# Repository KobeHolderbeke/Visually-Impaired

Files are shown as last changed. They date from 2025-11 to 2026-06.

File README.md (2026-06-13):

# Feel The Score
*Ontwikkelen van een handsfree, toegankelijk systeem dat slechtzienden en blinden helpt muziek intuïtief te leren en te spelen zonder afhankelijk te zijn van traditionele braillepartituren.* 

🛠️ Built by ``Kobe Holderbeke`` & ``Mattea Claeys``   
🔥 Supervised by ``prof. dr. Bas Baccarne``, ``Yannick Christiaens`` & ``Wouter Devriese``    
🌱 Grown at ``Ghent University`` 🏛️ ``Industrial Design Engineering`` ([project overview](https://github.com/basbaccarne/human-centered-design))       

*13/11/2025*   

## Samenvatting
### Probleem 

Slechtziende muzikanten stuiten op grote drempels bij het leren van nieuwe muziek. Braille-bladmuziek is namelijk een complexe, aparte taal die velen niet beheersen. Bovendien moeten muzikanten hun instrument constant loslaten om handmatig door braille-partituren te navigeren, wat de flow onderbreekt en frustratie uitlokt. 

### Onderzoek 

Dit probleem werd vastgesteld via een interview (N = 1). De interviewee stelde: “Ik heb dat (Braille Muziekschrift) wel geleerd, maar ik blijf er zoveel mogelijk van af”. Deze persoon speelt als alternatief de muzikale audiotrack af en leert het doormiddel van perfect pitch*.  

Er blijkt behoefte te zijn aan een efficiënte, handsfree leermethode.

### Oplossing 

Het antwoord op dit probleem is om de muziek in audiovorm, zijnde dat de muziek track of de audio partituur, controleerbaar te maken door de voeten, doormiddel van een slim product. 

### Impact 

Dit neemt zowel de kloof van het leren van een nieuwe taal weg, alsook de frustratie van het loslaten van het instrument, met als hoop het leerproces aangenamer te maken en meer slechtziende mensen aan te zetten om muziek te leren.  

*perfect pitch: Het vermogen om een bepaalde toonhoogte te identificeren of na te bootsen zonder gebruik te maken van een referentietoon.  





---

## Introductie
Dit project ging van start met een algemene challenge: “Spacial Experiences for Visually Impaired Populations”, het ontwikkelen van een slim product dat slechtzienden assisteert in een vorm van ruimtelijke oriëntatie.  

Er wordt gebruikgemaakt van een zekere methode (zie [Methodologie](./docs/methodologie.md)), welke het ontwerpproces opdeelt in vaste fasen.  

Tijdens de eerste fase, [Discovery](./docs/discovery.md), is binnen het ruime probleem (afgeleid uit de challenge), gezocht naar een specifieker deelprobleem: 

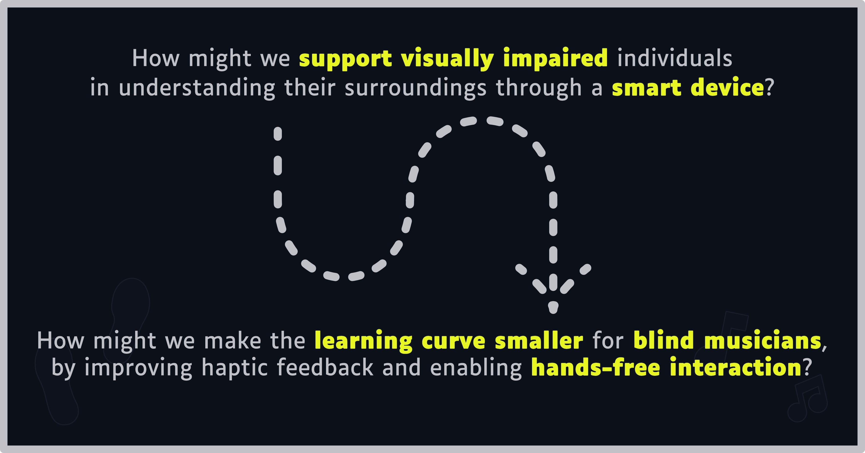
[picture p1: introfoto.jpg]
Introductie


Dit specifieker probleem kadert het project niet rond het vervullen van basisnoden zoals oriëntatie/koken/…, maar wel rond het ondersteunen van ontspanning en zelfexpressie voor slechtziende (aspirant-)muzikanten, door het leerproces van muziek voor hen aangenamer te maken. 
Het brengt volgende hoofddoelen met zich mee:
-	De gebruiker heeft geen kennis van een andere taal nodig, buiten notenleer.
-	De gebruiker moet tijdens het leren het instrument niet loslaten.
-	De gebruiker kan zowel een muziektrack als een audio partituur bedienen.
-	De (eventuele) bijhorende app moet voor slechtzienden toegankelijk zijn.

Ook de boundary conditions:
-	Het product signaleert gebruiksaspecten nooit enkel op visuele wijze.
-	Alle fasen moeten binnen de voorziene deadline (zie [Methodologie](./docs/methodologie.md)) afgewerkt worden.
Aan de hand hiervan wordt in de volgende fase, [Defintion](./docs/definition.md), nagedacht over hoe dit probleem het best kan opgelost worden. Uit inzichten van deze fase alsook uit de volgende fasen, worden zekere eisen geformuleerd waaraan het product moet voldoen (ook in welke mate noodzakelijk), namelijk de [Design Requirements](./docs/design_requirements.md) en ook welke materialen het best gebruikt worden en waar deze aangekocht worden, namelijk de een [Bill of materials](./docs/bom.md).

---

## Inhoudstafel

1. [Methodologie](./docs/methodologie.md)
2. [Discovery](./docs/discovery.md)
3. [Defintion](./docs/definition.md)
4. [Develop phase 1](./docs/Develop_1.md)
5. [Develop phase 2: Antropometrische analyse deel 1](./docs/Develop_phase_2:Antropometrie.md)
6. [Develop phase 2: Antropometrische analyse deel 2](./docs/Antropometrie2.md)
7. [Develop phase 2: Antropometrische analyse deel 3](./docs/Antropo3.md)
8. [Develop phase 2: Prototypes resultaten](./docs/DEV2result.md)
9. [Develop phase 2: Cognitieve analyse](./docs/CognitieveAnalyse.md)
10. [Develop phase 3: CMF Analyse](./docs/CMFanalyse.md)
11. [Develop phase 3: PESTEL Analyse](./docs/PESTELanalyse.md)
12. [Develop phase 3: Resultaten](./docs/DEV3results.md)
13. [Design Requirements](./docs/design_requirements.md)
14. [Bill of materials](./docs/bom.md)

## Conclusie

Het finale concept is een toegankelijke voetcontroller met bijhorende theoretisch uitgewerkte app die blinde en slechtziende muzikanten ondersteunt tijdens het zelfstandig oefenen. De controller maakt het mogelijk om een audio-partituur of muziekfragment te bedienen zonder de handen van het instrument te halen. Functies zoals pauzeren, hervatten, terugspoelen, doorspoelen en herhalen blijven daardoor bereikbaar tijdens het musiceren.

De keuze voor voetbediening sluit goed aan bij de muzikale context. Veel muzikanten zijn al vertrouwd met het gebruik van pedalen, waardoor deze manier van bedienen natuurlijker aanvoelt dan extra knoppen op een scherm of handmatige bediening. Het product vertrekt dus niet vanuit een volledig nieuwe interactie, maar bouwt verder op een handeling die binnen muziek al herkenbaar is.

De fysieke vormgeving is afgestemd op gebruik zonder zicht. Tactiel onderscheidbare knoppen, duidelijke voetpositionering, verstelbare muren, gripvaste materialen en een stabiele bodemplaat zorgen ervoor dat oriëntatie via gevoel mogelijk wordt. Ook de app ondersteunt toegankelijk gebruik door eenvoudige functies, duidelijke structuur en auditieve ondersteuning. Deze keuzes sluiten aan bij de opgestelde [design requirements](docs/design_requirements.md).

Dit concept vormt een sterke oplossing voor het eerder geschetste probleem, omdat het zelfstandigheid, gebruiksgemak en muzikale continuïteit combineert. Tijdens het oefenen ontstaat minder nood aan onderbreking of hulp van buitenaf. Tegelijk blijft het product bewust beperkt tot de belangrijkste functies, waardoor de bediening overzichtelijk blijft en de cognitieve belasting laag blijft.

Naast toegankelijkheid werd ook rekening gehouden met praktische aspecten zoals betaalbaarheid, robuustheid, onderhoud, transport en instelbaarheid voor verschillende lichaamsmaten. Het inklapbare ontwerp en de geïntegreerde handvaten maken het product bruikbaar in een thuis-, school- of oefencontext. Verdere validatie blijft nodig rond langdurig gebruik, materiaalkeuze, knopweerstand en exacte positionering van de bedieningselementen. Toch biedt dit finale concept een geloofwaardige en onderbouwde richting voor een toegankelijk hulpmiddel binnen muziekeducatie.

## Kritische reflectie
De samenwerking binnen de groep verliep vlot en de taken konden goed verdeeld worden. Daardoor konden verschillende onderdelen van het project tegelijk worden uitgewerkt, zoals onderzoek, prototyping, testen en documentatie. Toch had een vroegere planning het proces kunnen versterken, vooral bij het zoeken naar geschikte testpersonen.

Een belangrijke beperking was het beperkte aantal gebruikerstesten. Blinde en slechtziende muzikanten vormen een specifieke doelgroep die moeilijk te bereiken is. De testresultaten leverden daardoor waardevolle inzichten op, maar kunnen niet als volledig representatief gezien worden.

Ook het prototype vraagt nog verdere uitwerking en validatie. Vooral langdurig gebruik, knopweerstand, materiaalkeuze, stabiliteit en app-toegankelijkheid moeten verder getest worden. Daarnaast zijn de app en de render (foto bovenaan de main-page) voorlopig vooral conceptueel uitgewerkt. In een volgende fase kunnen deze onderdelen concreter gebouwd, getest en verfijnd worden. Het concept toont wel aan dat een handsfree voetcontroller een sterke richting kan zijn om zelfstandiger met audio-partituren te oefenen.

## Noot inzake het gebruik van AI
In dit project werd AI gebruikt voor spellings/grammatica controles van teksten en het omzetten van excel tabellen naar github tabellen. In hoofdstukken waarin AI voor andere doeleinden is gebruikt, wordt dit in het hoofdstuk zelf vermeld.

## Bijlagen

Voor een goede view van de bijlagen is openen van word bestanden in de desktop app aangeraden.

### Discovery
* Literatuuronderzoek (N=10)
  * [Protocol](https://ugentbe.sharepoint.com/:w:/t/Group.course1292876/IQB8WhhhP_pdSazPReRh-HxqAclnc3PnnkJyJq7oPYJ3NZ4?e=7g2boN)
  * [Rapport](https://ugentbe.sharepoint.com/:w:/t/Group.course1292876/IQB9HzvLZPKqSpc1Ftse8O0QARGRsxfzFwpFhsLdyy_mlFo?e=11EF0i)
* Interviews (N=3)
  * [Protocol](https://ugentbe.sharepoint.com/:w:/t/Group.course1292876/IQBQU56AthNHTY_BFFeUUjxmASiolwOdjGJiTEfFOpEcLPk?e=OsEMhK)
  * [Rapport](https://ugentbe.sharepoint.com/:w:/t/Group.course1292876/IQBf38VezsivToBSrIhYCN61AUVMqxSsOoYWdKP_1LEdgZQ?e=FsCly7)
    
### Definition
* User testing wave 1 (N=1)
  * [Protocol](https://ugentbe.sharepoint.com/:w:/t/Group.course1292876/IQCpgV68K8tYTbwqrU3BGaQVAbbZWw5pqcu_k0QDw4POE8I?e=BGHP7T)
  * [Rapport](https://ugentbe.sharepoint.com/:w:/t/Group.course1292876/IQAky_YwA6__RZtaeOcWHPhpASCxieU0GRjqjp9feo6laxo?e=5y6nlD)
* User testing wave 2 (N=1)
  * [Protocol](https://ugentbe.sharepoint.com/:w:/t/Group.course1292876/IQBjjLZSffDoT4YwZDXaZOrhAfhvxaoLlUYGOMogOBo6GUY?e=pMHGh2)
  * [Rapport](https://ugentbe.sharepoint.com/:w:/t/Group.course1292876/IQBcQqR74zqURJhRp2q5rA2XAcczsUglUP6ll5FD3lllPYg?e=BxCLvT)

 ### Develop phase 1
* User testing (N=3)
  * [Protocol](https://ugentbe.sharepoint.com/:w:/t/Group.course1292876/IQAjbiEWOX_lQ4XXfaun0UtAAUon7dIECnejuIu1gmOtWKU?e=WpIFe5)
  * [Rapport 1](https://ugentbe.sharepoint.com/:w:/t/Group.course1292876/IQDN2bwuJPMMSLmgR1tbd45yAW7m6enV3AymeFjA8X_QwLY?e=4EHN3X)
  * [Rapport 2](https://ugentbe.sharepoint.com/:w:/t/Group.course1292876/IQC0vbEEvfZeQ49qQybeRaqQAQ82UMk618w59HhCXBCYtpQ?e=vUupAp)

 ### Develop phase 2
* User testing (N=2)
  * [Protocol](https://ugentbe.sharepoint.com/:w:/t/Group.course1292876/IQApzxOackPtQ5DfW1NZEpZ_AazlX7PwUC5u7cyfCQHkbIs?e=VCITgi)
  * [Rapport](https://ugentbe.sharepoint.com/:w:/t/Group.course1292876/IQDsXy24CQZ0SruVJJgNmixlAYmxdDDpnKVGn1WYPvfYCAY?e=BnQCGx)
    
 ### Develop phase 3
* User testing (N=2)
  * [Protocol](https://ugentbe.sharepoint.com/:w:/t/Group.course1292876/IQDxzxEtF3QAR5I6zrbhMU4dAT4qlioyNcmz1yhkrsbSU70?e=lP8Dhw)
  * [Rapport](https://ugentbe.sharepoint.com/:w:/t/Group.course1292876/IQB-Db_cI9J0Srp22GOqeCKyAXsA48JMOGsO7cuSFgdweqc?e=k2Lcjh)

## Licentie

This repository contains both software and design materials created as part of an industrial design energineering project at Ghent University.

- **Software and code:** [MIT License](./LICENSE-MIT)  
- **Design, documentation, CAD, and media:** [CC BY 4.0 License](./LICENSE)
  
You are free to reuse and build upon this work, both commercially and non-commercially, as long as proper attribution is given to the original authors.

## Bronnen
 JohnSmith981. (2025, 7 december). *Absolute pitch*. In Wikipedia. https://en.wikipedia.org/wiki/Absolute_pitch

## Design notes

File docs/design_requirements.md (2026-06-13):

## Overzicht van Design Requirements
|| **Status** || ❌ niet voldaan || ⚠️ gedeeltelijk voldaan || ✅ voldaan ||
## Design Requirements

| **ID** | **Categorie** | **Design R** | **Source** | **Status** |
|---|---|---|---|---|
| AUD-01 | **Auditieve functionaliteit & leerproces** | Het product moet hoofdzakelijk auditieve feedback geven aan de gebruiker. | Interview + Literatuur | ✅ |
| AUD-02 |  | Het product moet ondersteuning bieden voor relatief en absoluut gehoor. | interview + Literatuur | ✅ |
| AUD-03 |  | Het product moet gebruik kunnen maken van talking-scores / audio-partituren. | User-Test 1/2 | ✅ |
| AUD-04 |  | Het product moet audio-partituren handsfree kunnen besturen. | User-Test 1/2 | ✅ |
| AUD-05 |  | Het product moet audio kunnen pauzeren en hervatten. | User-Test 1/2; CognitieveAnalyse.md | ✅ |
| AUD-06 |  | Het product moet audio kunnen door- en terugspoelen en daarbij duidelijke feedback geven. | User-Test 1/2 | ✅ |
| AUD-07 |  | Het product moet een loopfunctie bieden met een duidelijk begin- en eindpunt. | User-Test 1; CognitieveAnalyse.md | ✅ |
| AUD-08 |  | Het product moet onderbrekingen tijdens het oefenen zoveel mogelijk beperken. | Literatuur; discovery.md | ✅ |
| APP-01 | **App & interface** | De app moet intuïtief bedienbaar zijn. | User-Test 1/2 | ✅ |
| APP-02 |  | De belangrijkste app-inputs mogen niet onverwacht van plaats veranderen. | User-Test 2 | ✅ |
| APP-03 |  | De app moet duidelijk maken hoeveel knoppen of inputs per interface beschikbaar zijn. | User-Test 2 | ✅ |
| APP-04 |  | De app moet gelabelde knoppen hebben zodat oriëntatie met VoiceOver mogelijk is. | User-Test 1 | ✅ |
| APP-05 |  | De app moet een intuïtieve en verstaanbare manier bieden om door de muziekcatalogus te navigeren. | User-Test Develop phase 1; Develop_1.md | ✅ |
| APP-06 |  | De app moet een auditieve tutorial of uitleg aanbieden die aan en uit gezet kan worden. | User-Test 1 | ✅ |
| APP-07 |  | De app moet verwarring in lijsten beperken, bijvoorbeeld via duidelijke tabbladen of een vaste navigatiestructuur. | Develop_1.md | ✅ |
| APP-08 |  | Er moet een geschreven of auditief raadpleegbare handleiding beschikbaar zijn met de nodige besturingsinformatie. | Develop_1.md | ✅ |
| UX-01 | **Gebruiksgemak & cognitieve belasting** | Het product moet een lage cognitieve belasting hebben tijdens gebruik. | Literatuur; PESTELanalyse.md | ✅ |
| UX-02 |  | Het product moet intuïtieve inputs bieden voor iedere functie. | User-Test 2; PESTELanalyse.md | ✅ |
| UX-03 |  | Het product moet bruikbaar zijn zonder uitgebreide uitleg of training. | User-Test 1/2 | ✅ |
| UX-04 |  | Het product moet het aantal primaire bedieningsinputs beperken om complexiteit en foutgebruik te verminderen. | User-Test 2; PESTELanalyse.md | ✅ |
| UX-05 |  | De gebruiker moet functies kunnen aan- of uitzetten zodat een basis- en gevorderde gebruikservaring mogelijk is. | PESTELanalyse.md | ⚠️ |
| UX-06 |  | Het ontwerp moet inspelen op gewoontes van de gebruiker en onnodige functies vermijden. | User-Test 2 | ✅ |
| ACC-01 | **Toegankelijkheid & inclusie** | Het product moet bestuurbaar zijn met minimale tactiele leesvaardigheid. | Interview | ✅ |
| ACC-02 |  | Het product moet zonder handen bediend kunnen worden. | User-Test 1 | ✅ |
| ACC-03 |  | Het product moet zelfstandig bruikbaar zijn voor blinde en slechtziende gebruikers zonder visuele ondersteuning. | CMFanalyse.md; README.md | ✅ |
| ACC-04 |  | Het product mag nooit uitsluitend visueel communiceren; belangrijke informatie moet ook tactiel, auditief of haptisch waarneembaar zijn. | README.md; CMFanalyse.md | ✅ |
| ACC-05 |  | De kleuren moeten voldoende contrast bieden tussen basis, knoppen en markeringen voor slechtziende gebruikers. | CMFanalyse.md | ✅ |
| ANT-01 | **Antropometrische maatvoering** | Het ontwerp moet voetmaten van de volledige doelgroep ondersteunen: grootste voet mannen 18–65 P99 = 289 mm voetlengte en 114 mm voetbreedte; kleinste voet meisjes 6 P1 = 157 mm voetlengte en 60 mm voetbreedte. | Develop_phase_2:Antropometrie.md | ✅ |
| ANT-02 |  | Voor de bepaling van knop-/contactposities moeten de Belgische schattingen gebruikt worden: mannen 18–65 P99 = 216,5 mm ballengte en 25,8 mm verticale afstand tussen maximale breedtepunten; meisjes 6 P1 = 109,4 mm ballengte en 15,2 mm verticale afstand. | Develop_phase_2:Antropometrie.md | ✅ |
| ANT-03 |  | De contact-/inputranges moeten met veiligheidsmarge afgerond worden naar 30 mm en 40 mm; dit komt uit 24,9 mm → 30 mm en 35,5 mm → 40 mm. | Develop_phase_2:Antropometrie.md | ✅ |
| ANT-04 |  | De voet-tot-voetafstand moet de geschatte extremen van de doelgroep ondersteunen: 105 mm tot 340 mm, afgerond naar een instelbereik van 100 mm tot 350 mm. | Antropometrie2.md | ✅ |
| ANT-05 |  | De dimensionering van de voetplaatsing moet rekening houden met heupbreedtes: mannen 18–65 P99 = 430 mm, vrouwen 18–65 P99 = 483 mm, jongens 6 P1 = 175 mm en meisjes 6 P1 = 180 mm. | Antropometrie2.md | ✅ |
| ANT-06 |  | De hoogte van de muren moet onderbouwd worden met de geschatte maximale voethoogte: P99 instaphoogte = 70,4 mm en Belgische schatting = 76,68 mm; de gekozen muurhoogte blijft 30 mm. | Antropometrie2.md | ✅ |
| ANT-07 |  | De handvatdimensionering moet rekening houden met handmaten van de doelgroep: handlengte 109–218 mm, handbreedte 51–98 mm, maximale handdikte 36 mm en maximale vingerdikte 17,8 mm. | Antropo3.md | ✅ |
| PHY-01 | **Fysiek ontwerp & ergonomie** | Het product moet een stabiele ergonomische rustpositie bieden. | User-Test 1 | ✅ |
| PHY-02 |  | Het product moet signifiers bieden om plaatsing, oriëntatie en gebruik duidelijk te maken. | User-Test 2; definition.md | ⚠️ |
| PHY-03 |  | Er moet een duidelijk tactiel verschil zijn tussen voetzones en knop-/behuizingszones. | DEV2result.md | ⚠️ |
| PHY-04 |  | Het product moet zo compact mogelijk zijn, met voorkeur voor verticale compactheid boven horizontale compactheid. | User-Test Develop phase 1; Develop_1.md | ✅ |
| PHY-05 |  | De bediening moet zo weinig mogelijk voetverplaatsing vereisen. | User-Test Develop phase 1; Develop_1.md | ✅ |
| PHY-06 |  | Het product mag bij langdurig gebruik geen negatieve lichamelijke gevolgen veroorzaken, zoals krampen of pijn. | Develop_1.md | ✅ |
| PHY-07 |  | De knopposities moeten bruikbaar zijn voor een brede range aan voetgroottes. | Develop_phase_2:Antropometrie.md | ✅ |
| PHY-08 |  | De knoppen moeten bereikbaar zijn zonder oncomfortabele voetrotatie of overdreven voetverplaatsing. | Develop_phase_2:Antropometrie.md | ✅ |
| PHY-09 |  | De bodemplaat moet finaal 485 mm lang en 320 mm breed zijn. | Antropometrie2.md | ✅ |
| PHY-10 |  | De zijwaartse muren moeten de voeten begrenzen met een muurgedeelte van 160 mm lang en een klemstuk van 31 mm lang. | Antropometrie2.md | ✅ |
| PHY-11 |  | De muren moeten een breedte van 10 mm hebben; de klemstukjes moeten 4,6 mm breed/hoog zijn zodat ze met tolerantie in de roosters schuiven. | Antropometrie2.md | ✅ |
| BTN-01 | **Knoppen & inputgedrag** | Per voet moeten twee knopcontactzones voorzien worden: een kleine knop/contactrange van 30 mm en een grote knop/contactrange van 40 mm. | Develop_phase_2:Antropometrie.md; Antropometrie2.md | ✅ |
| BTN-02 |  | De knoppen moeten 20 mm hoog zijn, 10 mm dik zijn en in niet-ingedrukte stand ongeveer 7,7 mm uit de muur steken. | Antropometrie2.md | ✅ |
| BTN-03 |  | Het indrukinterval van de knop moet ongeveer 5 mm bedragen als balans tussen misinputpreventie, compactheid, stevigheid en snelheid. | Antropometrie2.md | ✅ |
| BTN-04 |  | De schuif-/behuizingslepjes van de knoppen moeten ongeveer 9,8–10 mm hoog zijn, aan beide zijden 15 mm lang zijn en een schuifstukdikte van 1,8 mm hebben. | Antropometrie2.md | ✅ |
| BTN-05 |  | Het product moet ongewenste interpretatie van gebruik zoveel mogelijk vermijden. | User-Test Develop phase 1; Develop_1.md | ✅ |
| BTN-06 |  | De bediening moet zo snel mogelijk reageren binnen de context van muziek oefenen. | User-Test Develop phase 1; Develop_1.md | ✅ |
| BTN-07 |  | Het product moet het risico op verkeerde inputs minimaliseren. | User-Test Develop phase 1; Develop_1.md | ✅ |
| BTN-08 |  | Het product moet een nauwkeurige response geven op inputs. | Develop_1.md | ✅ |
| BTN-09 |  | Het product moet een merkbare vorm van haptische of trilfeedback bieden op inputs. | User-Test Develop phase 1; Develop_1.md | ⚠️ |
| BTN-10 |  | De knoppen moeten tactiel duidelijk onderscheidbaar zijn door verschil in textuur, vorm, grootte of afwerking. | CMFanalyse.md | ⚠️ |
| BTN-11 |  | De knoppen moeten voldoende grip bieden zodat de voet niet wegglijdt tijdens het bedienen. | CMFanalyse.md | ✅ |
| BTN-12 |  | Pauzeren moet op de meest toegankelijke input geplaatst worden. | CognitieveAnalyse.md | ✅ |
| BTN-13 |  | Terugspoelen moet bij voorkeur links geplaatst worden, omdat gebruikers links spontaan met teruggaan associëren. | CognitieveAnalyse.md | ✅ |
| SAFE-01 | **Foutpreventie & veiligheid** | Het systeem moet misinputs opvangen zonder de flow van de gebruiker te onderbreken. | PESTELanalyse.md | ✅ |
| SAFE-02 |  | Bij gelijktijdig of foutief indrukken van knoppen mag geen ongewenste actie uitgevoerd worden. | PESTELanalyse.md | ✅ |
| SAFE-03 |  | Het ontwerp moet misinputs bij grotere voeten voorkomen door voldoende ruimte, geschikte knopweerstand of een aangepaste inputvorm. | Develop_phase_2:Antropometrie.md | ✅ |
| SAFE-04 |  | Het product moet een antisliponderzijde hebben, bijvoorbeeld rubberen voetjes of een rubberen laag. | CMFanalyse.md | ✅ |
| SAFE-05 |  | De randen en overgangen van de behuizing moeten veilig en afgerond afgewerkt zijn. | CMFanalyse.md | ✅ |
| ADJ-01 | **Instelbaarheid & modulariteit** | De voetplaatsing moet instelbaar zijn zodat verschillende voetbreedtes en voetafstanden comfortabel ondersteund worden. | Antropometrie2.md | ✅ |
| ADJ-02 |  | De verstelbaarheid van het product moet voelbaar en vanzelfsprekend zijn. | DEV2result.md | ✅ |
| ADJ-03 |  | De gebruiker moet tactiel kunnen voelen wanneer een onderdeel vast of los staat. | DEV2result.md | ✅ |
| ADJ-04 |  | Het verstellen van de muurtjes moet zonder losse onderdelen kunnen gebeuren. | DEV2result.md | ⚠️ |
| ADJ-05 |  | De knoppen en/of begrenzende muren moeten mee kunnen bewegen met de ingestelde voetpositie. | Antropometrie2.md | ✅ |
| ADJ-06 |  | De begrenzende muren moeten in elke instelling voldoende vast staan om de voet te geleiden en bedieningskrachten op te vangen. | Antropometrie2.md | ✅ |
| ADJ-07 |  | Onderdelen en elektronica moeten afzonderlijk vervangbaar zijn zodat niet het volledige product vervangen moet worden. | PESTELanalyse.md; CMFanalyse.md | ✅ |
| ADJ-08 |  | De verschuifbare muren moeten vastgezet worden in een dubbel roostersysteem met zowel een borgingsafstand als tussenborgingsafstand van 5 mm. | Antropometrie2.md | ✅ |
| ADJ-09 |  | De rail van het dubbele roostersysteem moet 42 mm hoog zijn. | Antropometrie2.md | ✅ |
| ADJ-10 |  | Het eerste rooster moet van 12 mm tot 22 mm boven de bodemplaat lopen, met 12–17 mm voor borging en 17–22 mm voor het schuifstuk. | Antropometrie2.md | ✅ |
| ADJ-11 |  | Het tweede rooster moet van 27 mm tot 37 mm boven de bodemplaat lopen, met 27–32 mm voor borging en 32–37 mm voor het schuifstuk. | Antropometrie2.md | ✅ |
| ADJ-12 |  | De kant van de rail bij de referentiemuur moet over de eerste 55 mm geen dubbel rooster bevatten, zodat de werking intuïtiever wordt en onnodige uitsluiting beperkt blijft. | Antropometrie2.md | ✅ |
| ADJ-13 |  | Eén van de vier muren moet volledig links, vanuit gebruikersperspectief, vast aan de rail staan als referentiemuur/nulpunt; de andere drie muren moeten verschuifbaar zijn. | Antropometrie2.md | ✅ |
| ADJ-14 |  | De rail moet een algehele dikte van 15 mm hebben, waarvan 10 mm massief is en 5 mm uit uitsnijdingen/groeven voor de roosters bestaat. | Antropometrie2.md | ✅ |
| ADJ-15 |  | De muren moeten stevig borgen met staven: 3 mm diameter voor verticale blokkering door het bovenste rooster en 5 mm diameter voor horizontale blokkering door de bodemplaat. | Antropometrie2.md | ✅ |
| ADJ-16 |  | De borgingsbouten en gaten moeten op tolerantie gedimensioneerd worden: verticale bout 5 mm met gat 5,1 mm; horizontale bout 2,8 mm met gat 3 mm. | Antropometrie2.md | ✅ |
| CMF-01 | **Materiaal, CMF & afwerking** | De knoppen moeten bij voorkeur gemaakt worden uit TPU of een gelijkaardig gripvast en slijtvast materiaal. | CMFanalyse.md | ⚠️ |
| CMF-02 |  | De behuizing moet stevig, vormvast en bestand zijn tegen gebruik op de grond. | CMFanalyse.md | ✅ |
| CMF-03 |  | De behuizing moet bij voorkeur gemaakt worden uit ABS-kunststof wegens de balans tussen kostprijs, sterkte, gewicht en produceerbaarheid. | CMFanalyse.md | ⚠️ |
| CMF-04 |  | De behuizing moet een matte afwerking hebben om reflecties voor slechtziende gebruikers te beperken. | CMFanalyse.md | ✅ |
| CMF-05 |  | De behuizing moet plaatselijk licht getextureerd zijn om tactiele herkenbaarheid te ondersteunen. | CMFanalyse.md | ⚠️ |
| CMF-06 |  | Het kleurgebruik moet beperkt en functioneel blijven zodat het product duidelijk en niet verwarrend oogt. | CMFanalyse.md | ✅ |
| DUR-01 | **Duurzaamheid & onderhoud** | Het product moet stevig en robuust genoeg zijn voor herhaald fysiek gebruik met de voeten. | PESTELanalyse.md; CMFanalyse.md | ✅ |
| DUR-02 |  | De zijkanten van de knoppen moeten bestand zijn tegen herhaald aantikken met de voet. | CMFanalyse.md | ✅ |
| DUR-03 |  | De gekozen materialen moeten slijtvast zijn en bestand tegen wrijving, druk, stof en vuil. | CMFanalyse.md | ✅ |
| DUR-04 |  | Het product moet eenvoudig schoon te maken zijn met een vochtige doek. | CMFanalyse.md | ⚠️ |
| DUR-05 |  | De texturen mogen niet te diep zijn, zodat stof en vuil zich niet gemakkelijk ophopen. | CMFanalyse.md | ✅ |
| DUR-06 |  | Het product moet zo weinig mogelijk naden, spleten en openingen bevatten. | CMFanalyse.md | ✅ |
| DUR-07 |  | Onderdelen die veel slijtage krijgen, zoals de knoppen, moeten indien mogelijk vervangbaar zijn. | CMFanalyse.md | ✅ |
| TRN-01 | **Transport & opbergen** | De bodemplaat moet inklapbaar of compact opbergbaar zijn zonder de bruikbaarheid tijdens het spelen te verminderen. | Antropometrie2.md | ✅ |
| TRN-02 |  | Het product moet automatisch of semiautomatisch beginnen dichtklappen wanneer het wordt opgetild. | DEV2result.md | ✅ |
| TRN-03 |  | Het handvat moet geïntegreerd blijven in de vorm van het product. | DEV2result.md | ✅ |
| TRN-04 |  | Het product moet stabiel blijven tijdens het ronddragen. | DEV2result.md | ✅ |
| TRN-05 |  | De bodemplaat moet in twee gelijke delen worden verdeeld met een horizontale snijlijn haaks op de voetlengterichting, zodat het prototype kan inklappen. | Antropometrie2.md | ✅ |
| TRN-06 |  | Aan weerszijden moeten handvatgaten voorzien worden die bij inklapping aligneren, zodat ze samen als één handvat gebruikt kunnen worden. | Antropometrie2.md | ✅ |
| TRN-07 |  | Het handvat moet een lengte van 100 mm krijgen zodat handen binnen de doelgroep in het handvat passen. | Antropo3.md | ✅ |
| TRN-08 |  | Het handvat moet een breedte/dikte van 35 mm over de kritische lengte krijgen zodat handen binnen de doelgroep comfortabel passen. | Antropo3.md | ✅ |
| TRN-09 |  | De handvat-tot-randafstand moet 22 mm bedragen zodat gebruikers binnen de doelgroep het product goed kunnen vastklemmen tijdens het dragen. | Antropo3.md | ✅ |
| BUS-01 | **Kostprijs & haalbaarheid** | De kostprijs moet laag genoeg blijven om het product toegankelijk te houden voor de doelgroep. | CMFanalyse.md; PESTELanalyse.md | ✅ |
| BUS-02 |  | De gewenste functionaliteit, robuustheid, contrast en textuur moeten tegen een zo laag mogelijke kostprijs bereikt worden. | PESTELanalyse.md | ✅ |
| DAT-01 | **Privacy & data** | De app moet zo weinig mogelijk persoonlijke gegevens opslaan en duidelijk communiceren welke data gebruikt wordt. | PESTELanalyse.md | ⚠️ |
| DAT-02 |  | Het ontwerp moet vermijden dat gebruikers een extra account moeten aanmaken, tenzij dit noodzakelijk blijkt uit gebruikerstests. | PESTELanalyse.md | ⚠️ |

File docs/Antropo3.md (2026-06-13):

# Develop 2 – Antropometrische Studie
## Deel III: Analyse van Handafmetingen – Dimensionering van handvat
### 1 Onderzoeksdoel

Het doel van dit onderzoek is om de plaatsing en afmetingen voor het handvat (Figuur 2) van een nieuwe prototype iteratie (Figuur 1) te definiëren. Zie Deel I: Analyse van Voetafmetingen – Dimensionering van Bakje en Deel II: Analyse van Heup- en Beenafmetingen – Plaatsing van Bakjes voor een beschrijving en conceptuele weergave van de verwachte functionaliteiten van dit prototype. Deze onbekenden worden bepaald doormiddel van een antropometrische analyse, gebruikmakend van bestaande betrouwbare antropometrische gegevens van de hand.

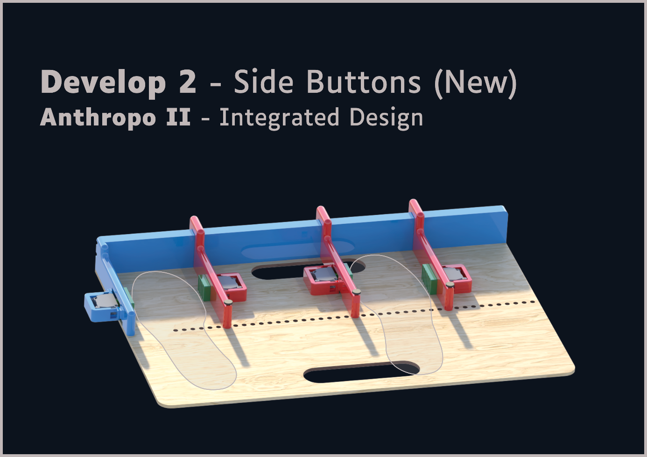
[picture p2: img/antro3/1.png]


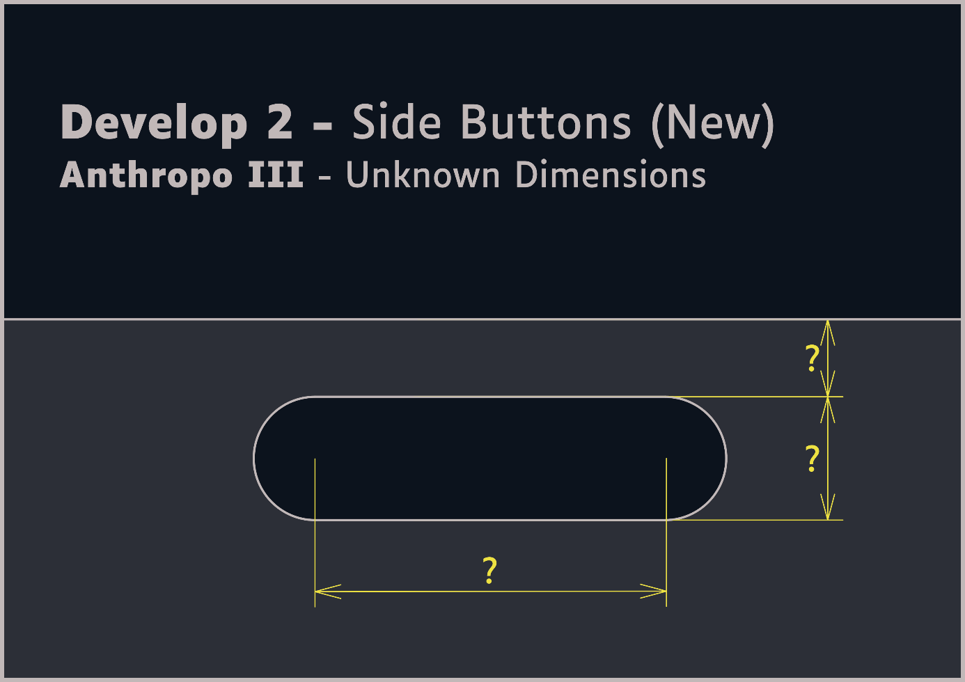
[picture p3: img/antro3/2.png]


### 2 Motivatie

Gezien de mogelijke toepassing dat dit product door muziekstudenten gebruikt zou worden en in naam van het algemene streefdoel om transportatie toegankelijk te maken, wordt gekozen om handvaten toe te voegen om hierbij te helpen. Het idee is niet om het horizontaal als een dienblad vast te houden, maar om de bodemplaat inklapbaar te maken, waardoor de handvaten langs weerskanten aligneren en het kan gedragen worden als soort handkoffer. Dit principe wordt in Figuur 3 afgebeeld.

Het is dan gewenst dat deze handvaten voor de gehele doelgroep voor ogen (“kleinste” jongens/meisjes van 6 jaar (P1) tot “grootste” mannen/vrouwen tussen de 18 en 65 jaar (P99)) bereikbaar en bruikbaar zijn, vandaar dit onderzoek.

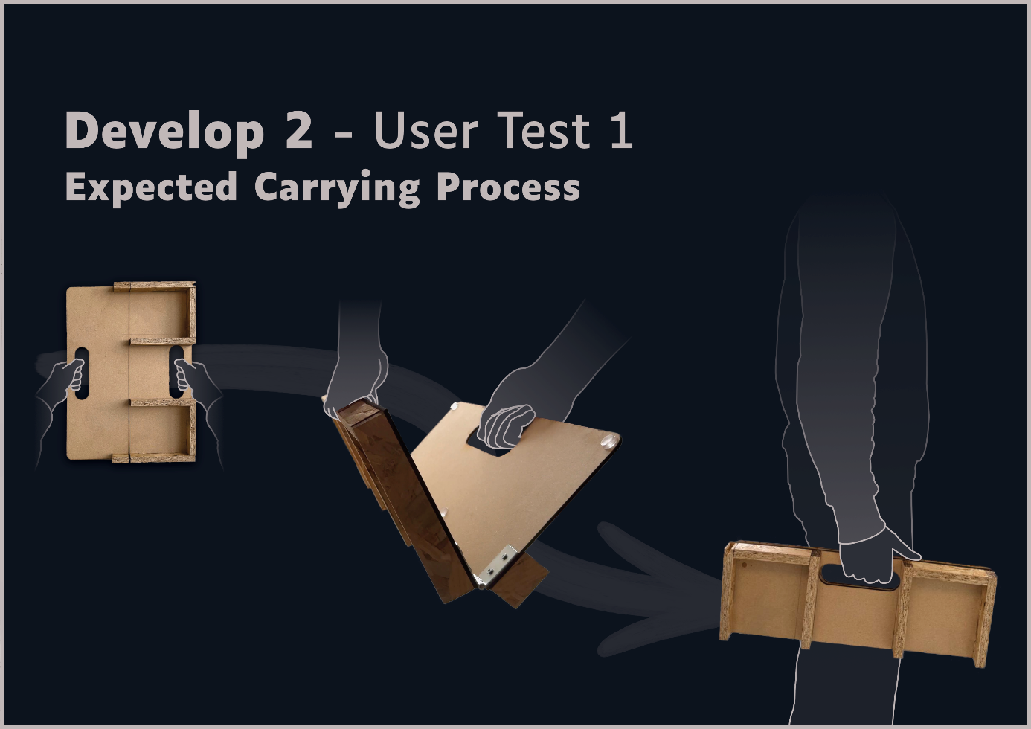
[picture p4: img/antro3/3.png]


### 3 Data

Als bron aan antropometrische gegevens wordt DINBelg gebruikt. 

De interessante gegevens zijn:
-	Handlengte
-	Handbreedte
-	Handdikte

Deze gegevens zijn verzameld in Tabel 1:

| Populatiebeschrijving | Handlengte (mm) | Handbreedte (mm) | Handdikte (mm) |
|---|---:|---:|---:|
| Mannen, 18-65, P99 | 218 | 98 | 36 |
| Vrouwen, 18-65, P99 | 202 | 85 | 33 |
| Jongens, 6, P1 | 111 | 51 | / |
| Meisjes, 6, P1 | 109 | 52 | / |

### 4 Data analyse

De handlengte varieert tussen 109mm en 218mm.

De handbreedte varieert tussen 51mm en 98mm.

De maximale handdikte is 36mm.

#### 4.1 Dimensionering van concept

Voor de lengte van het handvat wordt 100mm genomen, om de gehele range [51, 98] te accommoderen.

De breedte van het handvat wordt op 35mm genomen. Op het eerste zicht lijkt dit te klein aangezien de maximale handdikte 36mm is, maar in de holte van het handvat komen enkel de vingers terecht, niet het volledige hand.

De dikte van de hand aan de vingers wordt benaderd doormiddel van een antropometrische studie van Rogers et al. (2008). Hierin wordt de vingerdikte gemeten als de afstand tussen de palm en de rug van de vinger, aan de verschillende gewrichten. De maximale dikte hierbij bedraagt 17,8mm zelfs met een grote factor erbij gerekend in naam van onzekerheid van schatting, zal 35mm nog steeds ruim voldoende zijn.

Wat de implicaties van de handlengtes zijn, ligt ook iets complexer. Het prototype kan immers op verschillende manieren vastgehouden worden tijdens het ronddragen, zoals afgebeeld in Figuur 4:

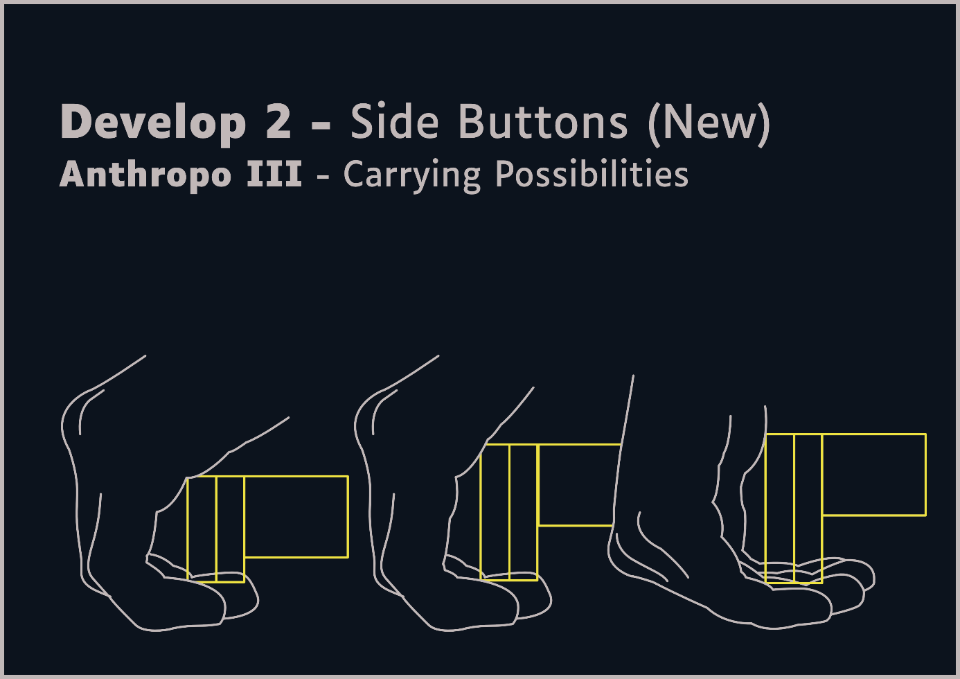
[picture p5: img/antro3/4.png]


Hoewel je in principe het prototype in de hand zou kunnen laten vallen, zonder deze bovenaan vast te klemmen, zoals te zien in de derde situatie van Figuur 4, kan dit voor discomfort zorgen, aangezien het gehele gewicht geconcentreerd is op hetzelfde punt, vergelijkbaar met het ronddragen van een plastic zak.

De grootste inklemming en bijgevolg gewichtsverdeling, zo ook comfort, is bij het vasthouden zoals in de eerste situatie van Figuur 4.

De inschatting wordt gemaakt dat zo’n inklemming haalbaar is als de te “overbruggen” afstand, dus de afstand tussen het handvat en de rand, ongeveer een vierde van de handlengte bedraagt.

Dit zou betekenen:

109mm * 1/4 =27,25mm

Rekening houdend met het feit dat deze schatting zuiver gebaseerd is op intuïtie, wordt gekozen voor een afstand van 22mm. Dit zou het product comfortabel vast neembaar moeten maken (testen ter validatie), zonder de structurele integriteit in gevaar te brengen. 

---

#### 4.2 Analyse van dimensionering

Hieruit volgen als samenvatting volgende dimensies:

  -	Handvatbreedte (minus afronding, dus enkel voor het stuk met eenzelfde breedte): 100mm

  -	Handvatdikte: 35mm

  -	Handvat-tot-rand afstand: 22mm
  
Deze dimensies worden ook verzameld en geïllustreerd in Figuur 5:

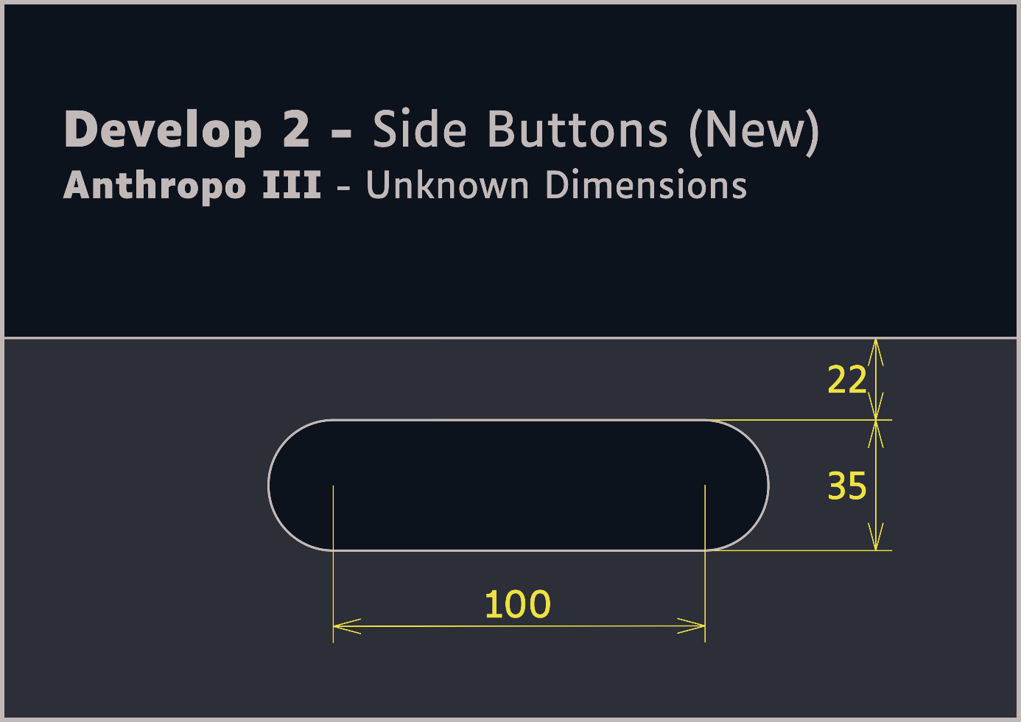
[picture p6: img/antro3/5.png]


---

### 5 Conclusie

Uit het onderzoek komen volgende nieuwe design requirements voort:

-	Om de handen van iedereen binnen de doelgroep in het handvat te laten passen, krijgt deze een lengte van 100mm.

-	Om de handen van iedereen binnen de doelgroep in het handvat te laten passen en comfortabel te laten zitten, krijgt deze een breedte van 35mm over de gehele kritische lengte.

-	Om iedereen binnen de doelgroep het product goed te laten vastklemmen bij het dragen, wordt de handvat-tot-rand lengte 22mm.

### 6 Literatuurlijst
#### 6.1 Internetpagina's

DINBelg. (2005). DINBelg. https://www.dinbelg.be
Rogers, M. S., Barr, A. B., Kasemsontitum, B., & Rempel, D. M. (2008). A three-dimensional anthropometric solid model of the hand based on landmark measurements. Ergonomics, 51(4), 511–526. https://doi.org/10.1080/00140130701710994 

#### 6.2 Generatieve AI

Generatieve AI (ChatGPT, OpenAI) is gebruikt ter ondersteuning bij het toepassen van APA-richtlijnen, waaronder het correct formatteren van bronvermeldingen en het verwijzen naar figuren en citaten. De output is gecontroleerd en waar nodig aangepast door de auteur.

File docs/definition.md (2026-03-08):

## Definition
Het doel van de Definition fase is om een antwoord te vinden op de vraag:  

_“Hoe kunnen we de leercurve voor slechtziende muzikanten verkleinen door de haptische feedback te verbeteren en interactie zonder handen mogelijk te maken?” [Introductie](/README.md)_ 

Dit vindt plaats onder de vorm van twee waves, door het volgen van een vast proces [Methodologie](/docs/methodologie.md): 
- Brainstormen _(Functies, vormgeving)_
- Schetsen _(Conceptuele uitwerking)_
- Prototypen _(Materialisatie)_
- Testen _(Validatie/verbetering/eliminatie, inzichten, N = 2)_

---
### Wave 1 

**Brainstorm** 

Er kon gewerkt worden met intuïtie, Discovery interviews en benchmarking om te veronderstellen wat het product zou moeten doen en hoe het er zoal zou kunnen uitzien. 

Eerst werden de functies bepaald: 

Het product moet de gebruiker in staat stellen de muziektrack, audiopartituur te kunnen: 
- Pauzeren
- Hervatten
- Doorspoelen
- Terugspoelen 

Voor de vormgeving waren relevante inzichten uit benchmarking dat compactheid een grote rol speelt en dat vaak gebruikgemaakt wordt van metaforen. _(vormen/functies van alledaagse producten die al bij mensen bekend zijn)._ 

Hierdoor kwam het idee van twee pedalen _(1 per voet)_, vergelijkbaar met gitaarpedalen: 

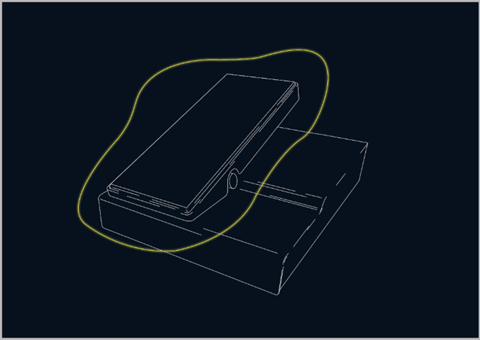
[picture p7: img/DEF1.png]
PEDAAL


**Schetsen** 

Rekening houdend met de vooropgestelde eigenschappen komt het schetsproces uit op 2 compacte indrukbare “blokjes”, geïnspireerd door gitaarpedalen. 

Zoals weergegeven bieden deze 2 pedalen genoeg inputmogelijkheden om de vooropgestelde functies te kunnen uitvoeren.

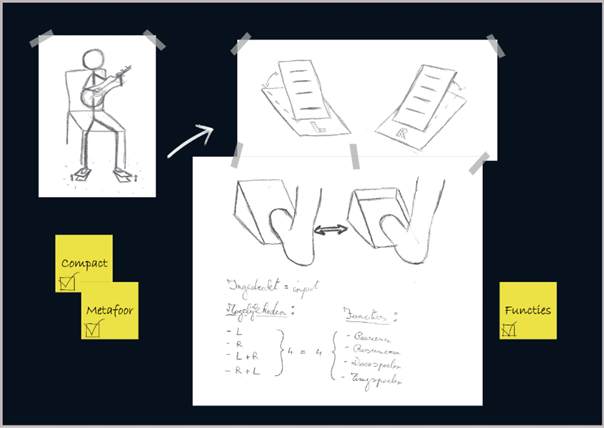
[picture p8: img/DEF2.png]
SCHETSEN
 

**Prototypen** 

De materialisatie gebeurt vooral uit karton, met willekeurig gevonden houten blokjes als gewichten en versneden gipsplaatpluggen als veringen. Doormiddel van reliëf wordt aangeduid waar de voet moet geplaatst worden en deze worden met een marker in een contrasterende kleur ingekleurd voor gebruikers die nog kleuren kunnen waarnemen. 

Er wordt ook een Makey Makey kit gebruikt met als hoop functionaliteit aan het prototype toe te voegen. De draden worden met plakband bevestigd en gepositioneerd zodanig dat deze contact maken bij indrukking. 

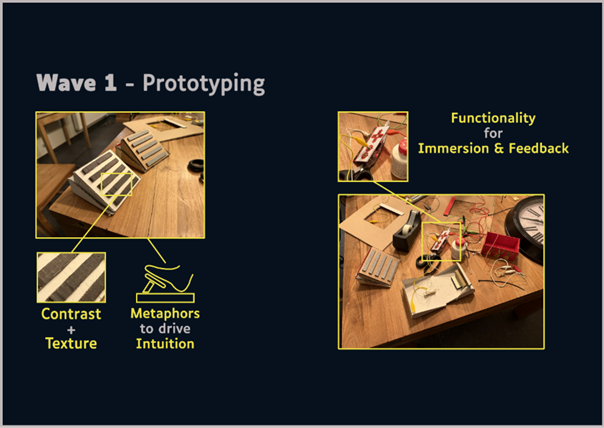
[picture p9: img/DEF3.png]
PROTOTYPE VISUAL
 

Bij een zelftest van het prototype werkt de Makey Makey zoals gewenst: bij aansluiting aan een laptop kan met de pedaal een video gepauzeerd en hervat worden. 

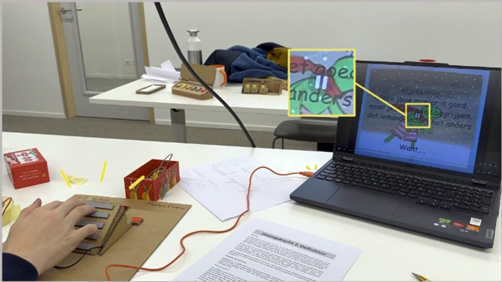
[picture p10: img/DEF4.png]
ZELFTEST
 

De Makey Makey is echter beperkt in welke outputs het van zichzelf aan de laptop kan overbrengen, namelijk: left-click, spatie en de pijltjestoetsen. 

Er blijken andere inputs dan deze nodig te zijn om de gewenste functies te behalen. 

E.g. deze van Mediaspeler: 
- Pauzeren	    -	Spatie
- Hervatten	   -	Spatie
- Doorspoelen	 -	Ctrl + Rechtse pijl
- Terugspoelen	-	Ctrl + Linkse pijl 

De Makey Makey biedt geen Ctrl output. Om dit te omzeilen wordt een extra input converter programma geïnstalleerd _(PowerToys)_: 

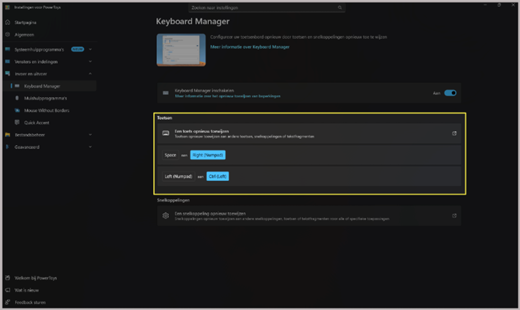
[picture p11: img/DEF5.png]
POWERTOYS
 

Bij het testen van de combinatie van de Makey Makey en PowerToys input converter, werkten de nieuwe inputs niet in Mediaspeler, noch in Spotify. Ook in Word was er geen werking.  

Dit betekent dat het testen van functionaliteit in deze fase beperkt wordt tot enkel pauzeren en hervatten en hiervoor in de volgende fase doormiddel van Arduino of het maken van een eigen mediaprogramma een andere oplossing moet gevonden worden.

**Prototypen – App** 

Het is een vaste constraint dat zowel muziektracks als audiopartituren door de gebruiker gekozen moeten kunnen worden. Echter is er geen enkele app waarin je van een nummer beide van deze opties kan selecteren.  

Er is wel een website met open-source code die partituurfiles omzet tot gesproken audiopartituren: https://www.talkingscores.org/.  

Met behulp hiervan zal dus een eigen app ontwikkeld moeten worden. 

Dit gebeurt in deze fase enkel theoretisch, in een Word document waarin alle inputs en outputs van de app beschreven staan. 

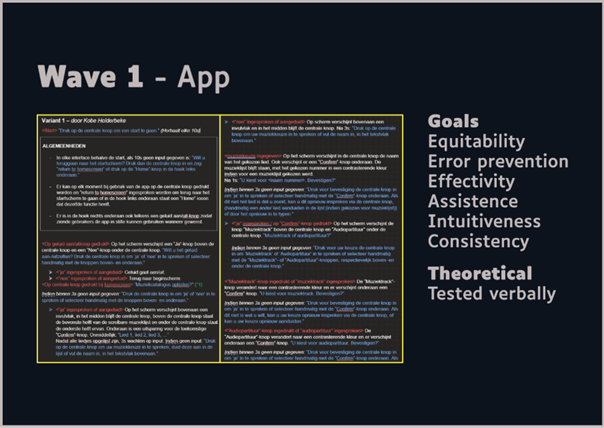
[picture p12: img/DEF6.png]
APP WAVE 1
 

Deze app wordt mondeling getest, waarin een onderzoeker zich voordoet als de app.

**Testen (Zie ook [Methodologie](/docs/methodologie.md))** 

<ins>Protocol</ins>  

De usability, intuïtiviteit van plaatsen/gebruiken, (hoeveelheid) misinputs, comfort bij gebruiken en frustratie/terughoudendheid/angst/… tijdens gebruik worden gemeten/getest bij de pedalen. 

Voor de app wordt geobserveerd of de gebruiker ergens vast komt te zitten of stappen terug hoeft te nemen, welke emoties er zijn bij gebruik en of de gewenste taak voltooid kan worden. 

Ook het volledige stappenplan van hoe de test verloopt staat beschreven. 

_Voor een volledige beschrijving, zie Wave 1 [Protocol](https://ugentbe.sharepoint.com/:w:/t/Group.course1292876/IQCpgV68K8tYTbwqrU3BGaQVAbbZWw5pqcu_k0QDw4POE8I?e=BGHP7T)_ 

<ins>Test</ins>

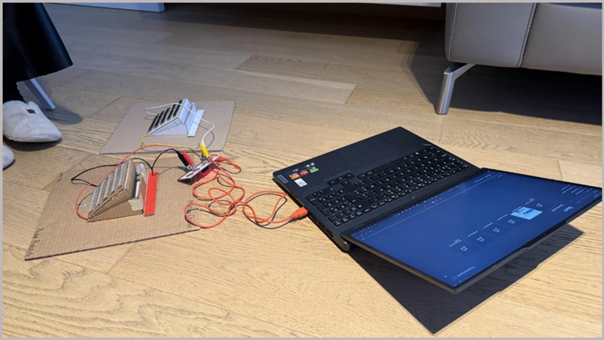
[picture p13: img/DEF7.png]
Test 1
 

<ins>Report</ins>

Key takeaways 
- Gebruiker was terughoudend bij gebruik -> Product moet sterker aanvoelen
- Geen onderscheid tussen linker- en rechterdeel -> Signalisatie van volgorde
- Looping functie overwegen
- Tijdens spelen kunnen wisselen tussen muziektrack en audiopartituur overwegen
- Meerdere inputs per voet overwegen
- Betere rustpositie op pedalen welke misinputs vermijdt
- Meer weerstand van pedaal overwegen
- Assisterende stem bij frequente gebruikers kan annoyance vormen -> Aparte optie om deze uit
  te zetten
- Settings knop toevoegen
  
_Voor een volledige beschrijving, zie Wave 1 [Report](https://ugentbe.sharepoint.com/:w:/t/Group.course1292876/IQAky_YwA6__RZtaeOcWHPhpASCxieU0GRjqjp9feo6laxo?e=5y6nlD)_

---
### Wave 2

**Brainstorm** 

De nieuwe inzichten/ideeën voor het prototype bekomen uit de eerste gebruikerstest worden in rekening genomen bij deze ideegeneratie, met name 2 inputs per voet, een neutrale, horizontale rustpositie, meer weerstand bij indrukking en een robuuster geheel.  

Ook wordt antropometrie nu toegepast. 

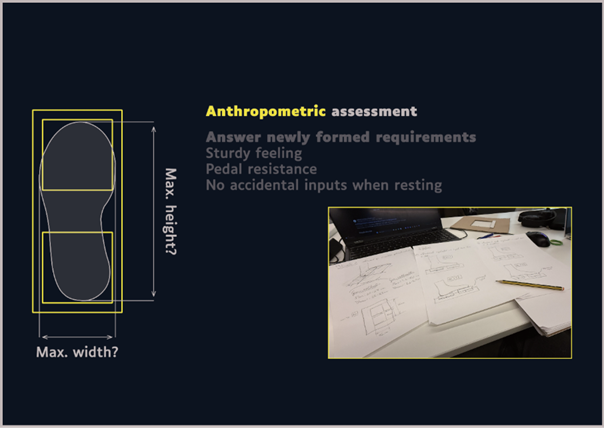
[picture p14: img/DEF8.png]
Brainstorm 2
 

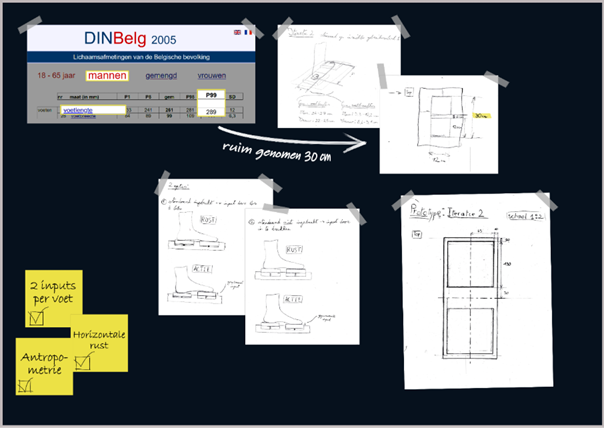
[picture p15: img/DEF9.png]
Antropometrie


**Prototypen** 

Zoals het eerste prototype wordt ook dit prototype gematerialiseerd uit vooral karton. Echter zijn het deze keer meerdere lagen op elkaar geplakt wat voor extra stevigheid zorgt. Ook is het veringmechanisme anders: hier worden elastieken (haarbandjes) gebruikt.

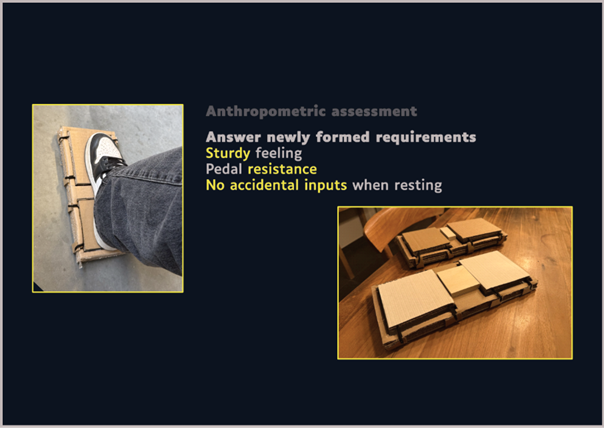
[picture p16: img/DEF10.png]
Prototyping 2


Aan de app wordt in het theoretische model een ‘Settings’-knop toegevoegd, alsook de optie om de spraakassistent aan/uit te zetten. 

**Testen (Zie ook [Methodologie](/docs/methodologie.md))** 

<ins>Protocol</ins>  

Dezelfde zaken als bij de vorige test worden opnieuw onderzocht, met nog een extra nadruk op de tekortkomingen van prototype 1. De loop van het onderzoek is voor een groot deel identiek. Zowel het eerste prototype (pedalen) als het nieuwe prototype worden getest.  

De prototypes worden onderling vergeleken op vlak van prestatie in de verschillende meetgebieden, zowel observerend als door de mening te vragen van de proefpersoon _(QAP)_. 

_Voor een volledige beschrijving, zie Wave 2 [Protocol](https://ugentbe.sharepoint.com/:w:/t/Group.course1292876/IQBjjLZSffDoT4YwZDXaZOrhAfhvxaoLlUYGOMogOBo6GUY?e=pMHGh2)._ 

<ins>Test</ins>

Prototype 2 presteerde ondermaats bij de opstellingstest.

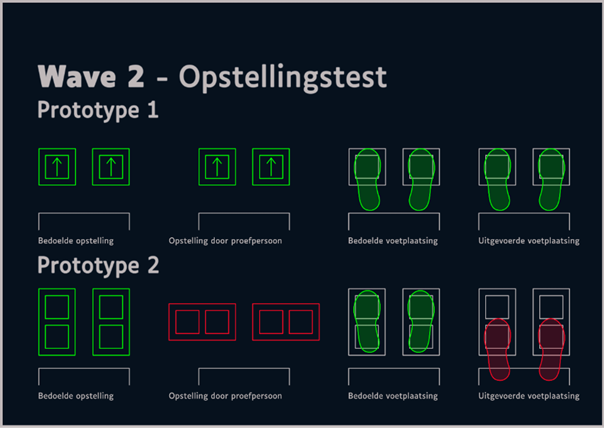
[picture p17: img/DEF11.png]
TEST 2


_QAP 
“Pedalen zijn makkelijk en compact.” 
“Prototype 2 is te complex, lomp en groot, maar betere druksensatie.”_ 

<ins>Report</ins>

Key takeaways 
- Balans vinden tussen complexiteit, functionaliteit en grootte
- Signaleer ordening, plaatsing en oriëntatie met textuur en vorm
- Eliminatie van intermediaire confirmatieschermen, met als substitutie “Return”-knop overwegen
  (App) 

_Voor een volledige beschrijving, zie Wave 2 [Report](https://ugentbe.sharepoint.com/:w:/t/Group.course1292876/IQBcQqR74zqURJhRp2q5rA2XAcczsUglUP6ll5FD3lllPYg?e=BxCLvT)._

---
### Convergence of waves

Gebaseerd op de takeaways van de 2 testen wordt een nieuw theoretisch prototype uitgewerkt om de Definition fase mee af te sluiten. 

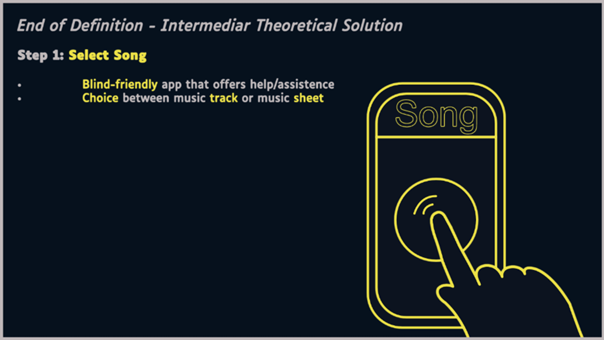
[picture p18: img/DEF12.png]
COW 1


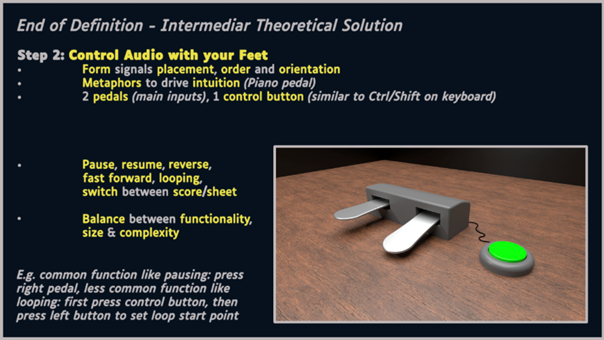
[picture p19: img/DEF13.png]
COW 2


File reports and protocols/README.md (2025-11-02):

Add PDF versions of your reports here.   
   
- ❗Make sure this data is pseudonomized (give an alias to your respondent)    
- ❗Don't share personal information here.   
- ❗For informed consents and other documents that contain personal information: Add links to a OndeDrive folder and only give access to teachers.

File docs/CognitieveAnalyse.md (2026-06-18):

# Develop 2 – Cognitieve analyse
## 1 Onderzoeksdoel

Het doel van dit onderzoek is het mappen van de functies die in Develop 1 zijn gekozen als noodzakelijke functies (zie figuur). 

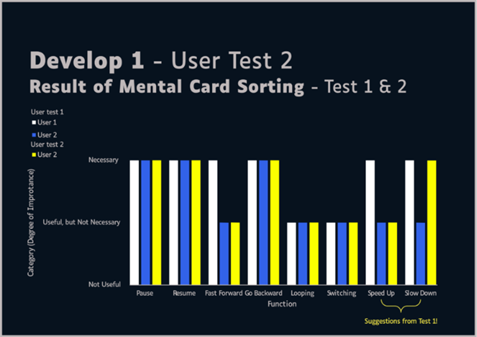
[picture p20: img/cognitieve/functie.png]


---
## 2 Motivatie

Omdat mensen met een visuele beperking sterk afhankelijk zijn van niet-visuele prikkels, is het noodzakelijk dat het prototype logisch, eenvoudig te begrijpen en zonder complexe handelingen te gebruiken is. Door de functies intuïtief te mappen kan het prototype gebruikt worden met minimale cognitieve belasting. Ook het instellen is een belangrijke factor om rekening mee te houden. Dit om frustraties, fouten en afhankelijkheid van anderen te vermijden.

---

## 3 Functiemapping

Voor gekeken wordt naar de mapping, is het interessant om te kijken naar hoe dit soort functies in het algemeen worden uitgevoerd. Dit kan aan de hand van de “Gulfs Of Execution and Evaluation” en de “7 stages of action”. 

Deze zaken kunnen worden toegepast op het pauzeren van een liedje/audiopartituur.

Execution gulf: kan de gebruiker de pauze-functie vinden en uitvoeren? 

Evaluation gulf: kan de gebruiker begrijpen dat de muziek gepauzeerd is?

Als dit iets dieper wordt uitgewerkt in de 7 stages wordt het resultaat verkregen in onderstaande figuur.

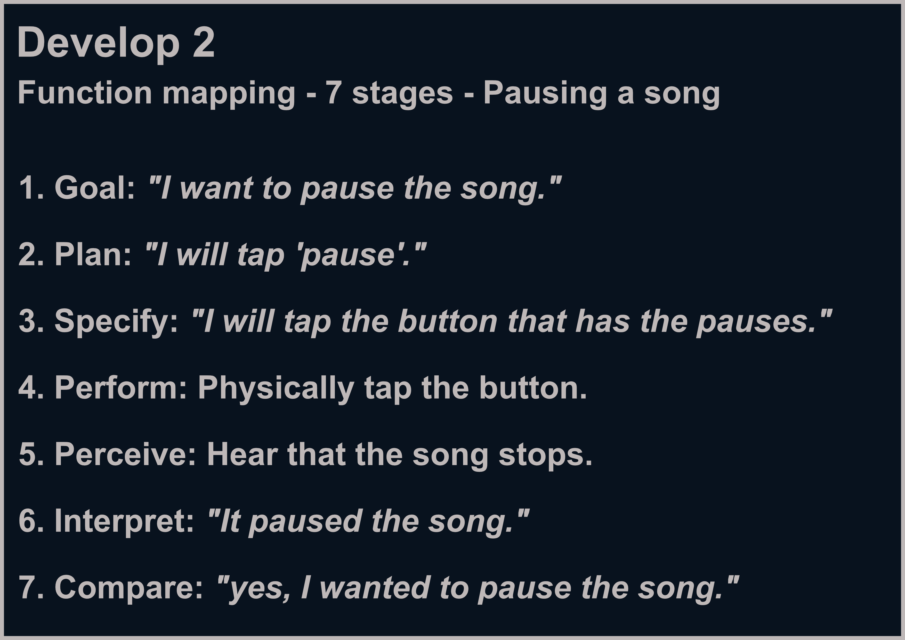
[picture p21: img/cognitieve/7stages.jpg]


Om te bepalen welke input(s) welke functie uitvoeren, kan gebruik worden gemaakt van twee methoden die vervolgens met elkaar worden vergeleken. Voor de eerste methode worden benchmarks uitgevoerd met andere producten en services om zo mogelijke patronen terug te vinden.

De andere methode card sorting net zoals werd gedaan bij de functies. Dit kan gebeuren door de proefpersonen een functie te geven en kijken welke input deze personen uiteindelijk indrukken. 

---

## 4 Benchmarking

Om dit te benchmarken moet gekeken worden naar welke services en producten gelijkaardige functies hebben. Deze functie en layout kunnen beschreven worden als enkele inputs die audio kunnen manipuleren (pauzeren, doorspoelen enzovoort). De basis layout van het te onderzoeken prototype is te vinden in onderstaande figuur.

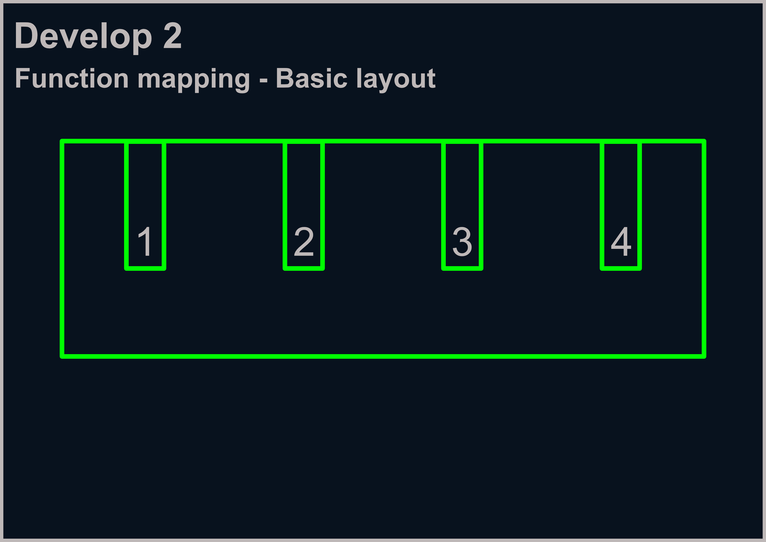
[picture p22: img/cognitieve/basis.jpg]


### 4.1 Service benchmarking

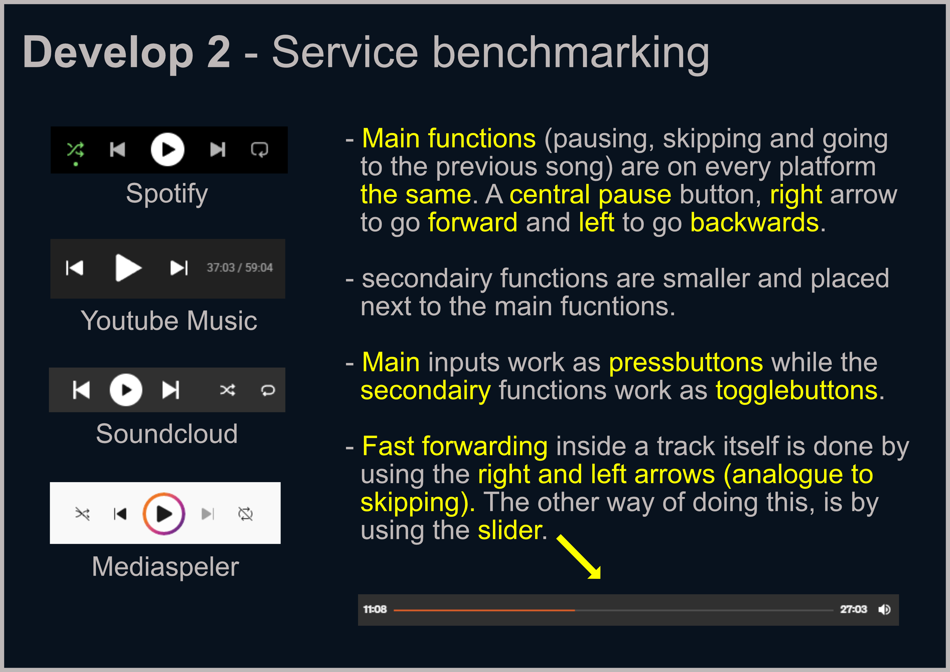
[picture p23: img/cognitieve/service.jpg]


### 4.2 Product benchmarking

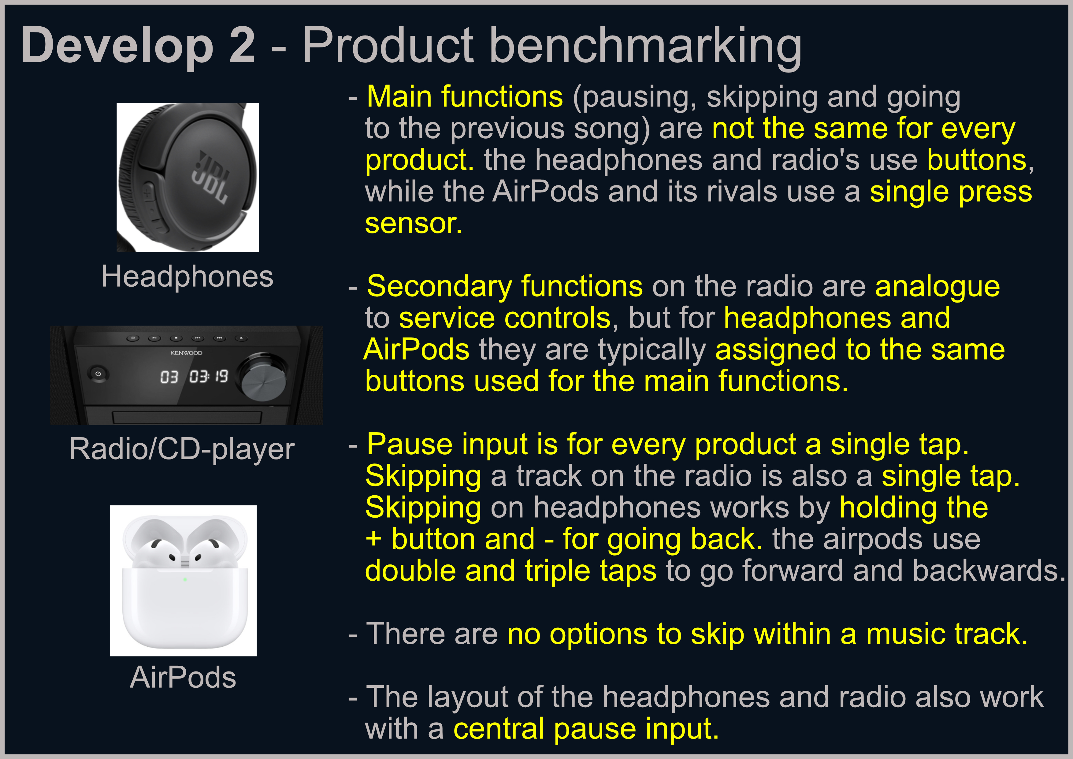
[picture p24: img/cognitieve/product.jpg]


### 4.3 conclusie

Uit de benchmarking komt duidelijk naar voren dat pauzeren zowel bij services als bij producten de meest toegankelijke functie is. Ook bij het instuderen van muziekstukken blijkt deze functie heel belangrijk. Tijdens de testen werd duidelijk dat blinde muzikanten meestal eerst naar een stuk muziek luisteren, daarna pauzeren en het vervolgens zelf proberen na te spelen. Daarom is het interessant dat de pauzeknop, net zoals in de benchmarking, centraal wordt geplaatst.

De knoppen om terug te spoelen, door te spoelen of de snelheid van de track aan te passen, bevinden zich meestal links en rechts van de pauzeknop. Daarbij wordt links vaak gekoppeld aan teruggaan en rechts aan verdergaan. Andere functies staan meestal verder weg van deze centrale knop, omdat ze minder vaak gebruikt worden.

Sommige extra functies worden ook niet altijd als aparte knop weergegeven. Ze zitten soms verwerkt in bestaande knoppen, bijvoorbeeld door een knop langer ingedrukt te houden of meerdere keren in te drukken. Op die manier blijft de bediening eenvoudig en overzichtelijk, met de pauzeknop als belangrijkste functie.

---

## 5 Interactieve cardsorting

Bij deze test koppelde de testpersoon zelf de eerder gekozen functies aan een bepaalde input. De testpersoon kreeg telkens een functie toegewezen, waarna werd gekeken met welke knop hij of zij deze functie spontaan verbond.

Daarna werd het systeem gesimuleerd door de inputs manueel te activeren via knoppen op een breadboard, op basis van de keuzes van de testpersoon (indien persoon knop 1 op het prototype indrukt, wordt knop 1 op het breadboard door een onderzoeker ingedrukt). Op die manier konden we nagaan welke opstelling voor deze specifieke gebruiker het meest logisch en gebruiksvriendelijk aanvoelde (zie figuur 6).

Als de gebruiker niet tevreden was met het resultaat, werd na de simulatie gevraagd welke aanpassingen nodig waren. Vervolgens werd de aangepaste opstelling opnieuw gesimuleerd. Dit proces werd herhaald tot de testpersoon tevreden was met de bediening.

_Opmerking: Deze test wordt uitgevoerd om in kaart te brengen wat de intuïtieve keuzes zijn voor blinde mensen. Als een functie op een specifieke knop wordt geplaatst is het interessantste van deze keuze de redenering waarom deze keuze werd gemaakt. Het doel is dus niet om gewoonweg de uitkomst te kopiëren in het eindproduct._

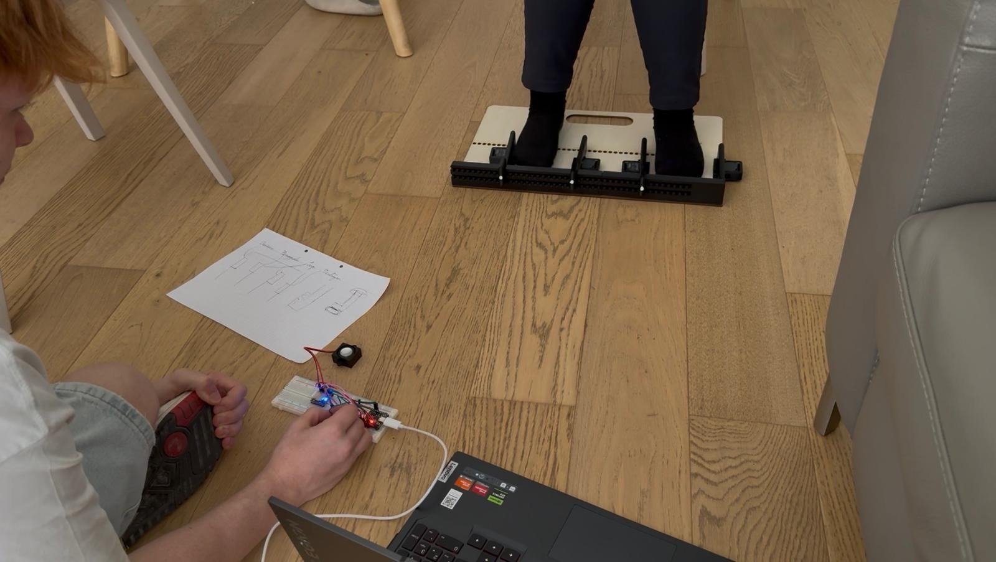
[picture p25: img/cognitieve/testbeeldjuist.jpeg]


### 5.1 Resultaat test 1



De gebruiker plaatste enkele functies op intuïtie. Rewinding of terugspoelen werd links geplaats doordat de gebruiker dit gewoon is. Ook de looping was gekozen op intuïtie met als metafoor een cassetterecorder. Waarbij je een knop moet indrukken om iets op te nemen. De pauzeer knop werd voor deze persoon geplaatst met de reden “makkelijkst bereikbaar voor mij”. De functie die de muziek sneller en trager laat afspelen werd willekeurig geplaatst op één van de overige knoppen, zonder bijkomende redenering.

Belangrijkste ondervindingen:
-	Links krijgt voorkeur als het over terugspoelen gaat 
-	Pauzeren zit op de meest toegankelijke plaats
-	Looping wordt geassocieerd met het blijven indrukken van een input zodat het gewenste stuk wordt opgenomen. 

### 5.2 Resultaat test 2



Bij de tweede test werd eerst en vooral terugspoelen terug met de linkse kant geassocieerd. Pauzeren kreeg twee knoppen, niet zozeer met de gedachte van “makkelijkst bereikbaar”, maar met de gedachte van “heb ik het meest nodig”. Het vertragen en versnellen werd hier geassocieerd met de rechter kant, maar hier moet kritisch gekeken worden. In de test werd per ongeluk vermeld dat de track niet wordt vertraagd bij het deel dat de muziek op dat specifiek moment is, maar dat er wordt geskipt naar een volgende track die trager wordt afgepeeld. De gebruiker kan hier dus de keuze voor de rechter kant hebben gemaakt met het gedacht voor door te spoelen. 
De looping werd weer verbonden aan een metafoor, namelijk een voice-recording op een smartphone. De testpersoon redeneerde dat het stuk dat gelooped moet worden, een begin- en eindpunt nodig heeft. De input voor deze punten te definiëren is tweemaal dezelfde, net zoals dat bij de knop van een voice-recording (of video opname als ander voorbeeld).

Belangrijkste ondervindingen:
-	Pauzeren wordt het meest gebruikt
-	Links krijgt voorkeur als het over terugspoelen gaat 
-	Looping werkt op intuïtie met een begin- en eindpunt

---

## 6 Conclusie - Verwerking van data

Voor het verwerken van de data moet de eerste stap de analyse zijn waarom bepaalde knoppen bepaalde functies krijgen bij zowel de benchmarking als de testdata. Enkele overlappingen zijn duidelijk. 

Bij zowel services, producten, maar ook bij de intuïtie van de testpersonen wordt pauzeren op de meest toegankelijke input geplaats. Dit zijnde de centrale knop bij een streaming service of de eenvoudigste input bij een product (vb. 1 tap op het oortje van de AirPod), maar ook de testpersonen plaatsten pauzeren op de meest toegankelijke plaats zonder invloed van andere. 

Terugspoelen werd bij zowel de benchmarking en testen gekoppeld aan de linker kant/voet. Hierop is één uitzondering, zijnde een AirPod: Hier moet driemaal getikt worden op het oortje, maar dit is hoofdzakelijk een gevolg van hardware keuzes.

Looping van een bepaald deel kwam bij de benchmarking niet voor (het herhalen van een liedje wel), maar hier kunnen naar voorbeelden gekeken worden die overeenkomen met de metaforen van de gebruikers. Deze zijn een cassetterecorder en een voice-recorder. De gelijkenis tussen deze twee voorbeelden is dat er een manier moet zijn waarvoor een bepaald stuk kan opgenomen worden die vervolgens wordt gelooped. Dit kan bijvoorbeeld door een input te geven over het gehele deel die moet opgenomen worden. Of door een input te geven aan het begin- en eindpunt van het gewenste deel. 

Voor het vertragen van de muziek kunnen de testpersona niet meteen een link leggen met een intuïtief idee voor welke knop deze functie kan uitvoeren. Als we naar benchmarking kijken voor functies die minder vaak gebruikt worden, is duidelijk dat deze altijd minder toegankelijk zijn, omdat ze kleiner zijn of een ingewikkeldere input nodig hebben. Bijvoorbeeld een kleinere knop op een streaming service die toggled tussen shuffelen of niet, of bij een koptelefoon waar een iets moeilijker gelegen knop kan toggelen tussen noise canceling of geen.

### 6.1 Eind opstelling



De uiteindelijke keuzes:
-	Pauzeren centraal beide knoppen (enkele press, toggle)
    -	Makkelijk bereikbaar
    -	Meest gebruikt
-	Terugspoelen links (enkele press)
    -	Intuïtief door gewoonten van gebruiker 
    -	Meeste producten/services
-	Vertragen (enkele press, toggle on/off)
    -	Minder gebruikte functie, dus principe eenvoudig houden als deze minder rap een gewoonte         wordt.
-	Looping (ingedrukt houden)
    -	Ingedrukt houden, want in totaal maar één input, dus beter voor fout gevoeligheid.

De beschrijving van hoe deze code tewerk gaat is [hier](https://github.com/MatteaClaeys/Opkomende_Tech_MC_KH) te vinden

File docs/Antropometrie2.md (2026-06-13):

# Develop 2 – Antropometrische Studie
## Deel II: Analyse van Heup– en Beenafmetingen - Plaatsing van Bakjes
### 1 Onderzoeksdoel

Het doel van dit onderzoek is om de afstand(en) tussen de bakjes van een nieuwe prototype iteratie (aangeduid met rood op Figuur 1) te definiëren. Zie Deel I: Analyse van Voetafmetingen – Dimensionering van Bakje voor een beschrijving en conceptuele weergave van de verwachte functionaliteiten van dit prototype. Deze onbekende dimensie(s) wordt/worden bepaald doormiddel van een antropometrische analyse, gebruikmakend van bestaande betrouwbare antropometrische gegevens.



*Figuur 1: Theoretisch model waarvan de afmeting(en) in het rood in dit onderzoek gedefinieerd worden*

---
### 2 Motivatie

Voor deze toepassing wordt een antropometrische analyse als noodzakelijk beschouwd, enerzijds omwille van het feit dat het onderzoeksproces zich in de tweede deelfase van de ontwikkelingsfase bevindt, waardoor van “quick and dirty” prototyping meer overgegaan moet worden tot iets degelijkere, beter uitgewerkte ontwerpiteraties. Anderzijds omwille van het feit dat de afstand tussen de bakjes om door (bijna) alle mensen bruikbaar te kunnen zijn, zeer moeilijk intuïtief te bepalen is. Deze data zijn ook nog verder in het proces bruikbaar, in het geval dat niet met dit concept verdergegaan wordt.

---
### 3 Data
Als bron aan antropometrische gegevens wordt DINBelg gebruikt. 

DINBelg biedt geen eenduidige gegevens voor de voet-tot-voetafstand in ruststand.

Als gevolg wordt deze afstand op basis van de heupbreedte geschat, met een factor 0,6 à 0,7 als verhoudingscoëfficiënt (zie Figuur 2 ter illustratie).



*Figuur 2: Benadering van voet-tot-voetlengte in rustende zitstand doormiddel van de heupbreedte*

De afname van nauwkeurigheid die deze aanname introduceert, dient weggewerkt te worden door genoeg speling op beide extrema te voorzien.

Voor de grootste voet-tot-voetafstand worden de maximale heupbreedtes van beide geslachten tussen 18 tot 65 jaar, binnen het 99ste percentiel (P99) vergeleken. De afstand wordt dan geschat door de grootste maat met de factor 0,7 te vermenigvuldigen.

Hetzelfde gebeurt voor de kleinste voet-tot-voetafstand, maar dan voor kinderen van 6 jaar, binnen het 1ste percentiel (P1). De afstand wordt dan geschat door de kleinste maat met de factor 0,6 te vermenigvuldigen.

De verzameling aan gegevens, alsook de overeenstemmende benaderde voet-tot-voetlengtes, zijn verzameld in Tabel 1.

*Tabel 1: Antropometrische gegevens van voetdimensies uit DINBelg*

| Populatiebeschrijving | Heupbreedte (mm) | Benaderde voet-tot-voetlengte (mm) |
|---|---:|---:|
| Mannen, 18-65, P99 | 430 |  |
| Vrouwen, 18-65, P99 | 483 | 338,1 ≈ 340 |
| Jongens, 6, P1 | 175 | 105 |
| Meisjes, 6, P1 | 180 |  |

---
### 4 Data analyse

De benadering van de voet-tot-voetafstand varieert tussen 105mm en 340mm voor de gekozen extremumgroepen. 

---
#### 4.1 Dimensionering van concept

De onnauwkeurigheid door de benadering wordt weggewerkt door beide verder in de richting van hun resp. extremum af te ronden:
-	Minimum: 105mm -> 100mm  
-	Maximum: 340 -> 350mm

De dimensies van de bakjes zijn te vinden in Deel I: Analyse van Voetafmetingen – Dimensionering van Bakje. Deze nieuwe waarden vormen de afstanden tussen de middens van de bakjes, zoals geïllustreerd in Figuur 1.

---
#### 4.2 Analyse van dimensionering

Beide edge cases: tall en small, worden geanalyseerd.

---
##### 4.2.1 Edge case: Design for the small

Bij de kleinste genomen voet-tot-voetafstand duikt mogelijks een probleem op. De bakjes zijn zodanig breed als gevolg van de vereiste om de grootste voeten (man, 18 - 65 jaar, P99) te kunnen accommoderen, dat deze kleinste afstand, bepaald in 4.1., niet bereikt kan worden. De bakjes overlappen deels.

Deze situatie wordt in Figuur 3 weergegeven, met de overlapping in het rood:



*Figuur 3: Analyse van edge case MIN waarin een potentieel probleem wordt aangetroffen*

Als de bakjes met huidige afmetingen zouden uitgewerkt worden in vaste vorm, zou de minimale toegelaten voet-tot-voetafstand vergroten tot 130mm tegenover de gewenste 100mm, wat een zeker deel van de groep zou “uitsluiten” (zie Figuur 4). 

ALS dit een probleem vormt, kan er op enkele manieren mee omgegaan worden:

  1.	Accepteer de “uitsluiting” van het betroffen deel van de groep en ga verder met huidige         ontwerpvisie.
  2.	Maak de vereisten minder streng.
  3.	Verander het ontwerp om dit deel van de groep toch niet uit te sluiten.



*Figuur 4: Minimale voet-tot-voetafstand voor de bakjes, toegelaten door het huidig ontwerp*

Om te kunnen beslissen of deze limiet aan minimale afstand effectief een probleem vormt, moet bepaald worden of er effectief sprake is van een uitsluiting of niet. De genomen voet-tot-voetafstanden zijn namelijk referenties maar niet bindend voor gebruik. Hierop wordt verder dieper ingegaan:

De afstand tussen de bakjes is tot nog toe bepaald doormiddel van de voet-tot-voetafstand van een persoon in rustende zithouding. Dit betekent met de benen naar voor staand, zoals afgebeeld in Figuur 5:



*Figuur 5: Weergave van hetgeen bedoeld wordt met “neutrale zitpositie”*

Het gebruik van deze neutrale zitpositie als gegeven voor een groep is zinvol voor de maximale afstandsmaat, om te bepalen hoe klein het mag zijn, zodat het nog steeds comfortabel bedienbaar is door de personen met de grootste voeten (maximale compactheid bereiken). Dit is echter niet bindend in de zin dat het product enkel bedienbaar is in deze positie.

De benen kunnen uitwijken langs de zijkant en tot op een bepaalde uitwijking is dit theoretisch gezien nog steeds comfortabel bedienbaar.

Om te bepalen wat deze maximale comfortabele uitwijking is, wordt de Comfort Analysis van Dreyfuss 3D uitgevoerd, ook binnen het Human Body Toolpakket van NX. De relevante resultaten hiervan zijn weergegeven in Figuur 6:



*Figuur 6: Resultaten van comfort analyse, betreffende de maximale comfortabele uitwijking van benen in rustende zitpositie*

Opmerkingen: 
  1.	Met de Human Body tool kunnen geen mensen jonger dan 18 jaar gegenereerd worden. Ook is
     geen Belgische data bruikbaar (Duitse data komt wel sterk overeen). Deze analyse geeft een
    	goed idee maar is dus geen analyse die 100% overeenstemt met de onderzochte groepen (6
    	tot 11 à 12-jarige Belgen).
  3.	Comfort van de enkels bij draaien van de voet is geen metriek die door de comfortanalyse
     onderzocht wordt. Echter is een uitwijking zo klein als 11 graden al genoeg voor bediening
    	en hiervan wordt verondersteld dat het geen discomfort zal bieden.

Zonder specifieke berekeningen uit te voeren, kan al gesteld worden dat de voeten comfortabel plaatsbaar zijn, met een voet-tot-voetafstand die op zijn minst overeenstemt met de heupbreedte.

De P1 heupbreedtes van jongens en meisjes van 6 jaar zijn resp. 175mm en 180mm (zie Tabel 1). Dit terwijl de nieuwe kritische afstand slechts 130mm bedraagt (Figuur 4).

**Met deze gegevens is het dus zeer veilig om te stellen dat deze geometrische beperking geen problemen zal bieden bij gebruik voor de kleinere groepen. Er worden geen nieuwe groepen uitgesloten.**

---
##### 4.2.2 Edge case: Design for the Tall

Figuur 7 biedt een weergave van de grootst genomen voet-tot-voetafstand, toegepast op het ontwerp:



*Figuur 7: Maximale voet-tot-voetafstand voor de bakjes*

---
##### 4.2.3 Vergelijking van edge cases

Als basis om te bepalen welke implicaties deze uiterste afstanden hebben op het ontwerp, worden ze bij elkaar gevoegd om te vergelijken. Dit is afgebeeld in Figuur 8:



*Figuur 8: Vergelijking van maximale en minimale voet-tot-voetafstand voor de bakjes*

---
##### 4.2.4 Implicaties van edge cases op ontwerp
###### 4.2.4.1 Design strategie

Het interval waarbinnen de voet-tot-voetafstanden liggen is [130, 350]. De ideale afstand voor de gemiddelde persoon binnen de groep waarvoor ontworpen wordt, ligt gezien ergens op een punt hierbinnen.

Het ontwerp moet dus niet enkel deze uiterste afstanden kunnen bieden, maar ook deze hiertussen, al dan niet met zekere intervallen.

Het is vanzelfsprekend dat in deze situatie gekozen wordt voor de design strategie design for adjustability. Anders zou immers design for the tall de enige overblijvende keuze zijn welke de hele groep includeert en dit zou tot veel te brede, onbruikbare en onhandige pedalen leiden, zoals geïllustreerd in Figuur 9:



*Figuur 9: Redeneringsproces en illustratie, welke de designstrategie design for the tall verwerpen en design for adjustability als beste keuze selecteren*

---
###### 4.2.4.2 Implicaties van design strategie

Design for adjustability als designstrategie kiezen voor dit ontwerp houdt in dat het instelbaar moet gemaakt worden binnenin het interval van extrema. De plaats waar de voeten komen moet hiertussen ingesteld kunnen worden.

Constraints hierbij om functionaliteit van het product te behouden:

1.	De knoppen moeten (de optie bieden) om op eender welke instellocatie even makkelijk
    bereikbaar te blijven door de voet(en).
->	De knoppen bewegen mee met de instelling of bieden in ieder geval deze optie. 

2.	De muren moeten (de optie bieden) om op eender welke instellocatie de voet(en) te
    begrenzen/constrainen/vasthouden, en de knoppen blijven behuizen.
->	Muren bewegen mee met de instelling of bieden in ieder geval de optie en zijn bij deze
  	instelling vast genoeg om de voet vast te blijven houden en tegen een stootje te kunnen,
  	bijvoorbeeld wanneer het kracht ondervindt als een knop wordt ingedrukt.

---
#### 4.3 Conceptgeneratie

Het conceptualisatieproces en de resultaten, gebruikmakend van de bekomen designimplicaties en dimensionering worden hier beschreven.

---
##### 4.3.1 Algemene principes

De constraints leggen vast dat de muren en de knoppen mee ingesteld moeten kunnen worden met de instelling van voetplaatsing en dat de muren in elk van de mogelijke instellingen vast genoeg moet staan zodat ze de voeten kunnen vasthouden en niet bewegen tijdens bijvoorbeeld het indrukken van de knoppen.

Met dit in gedachten wordt geopteerd voor een interval schuifsysteem. Een intervalsysteem heeft namelijk enkele voordelen boven continue instellingen:

-	Het instelstuk kan beter geborgd worden, met name zijwaartse borging, welke met continue
  instelling moeilijker te bereiken is. Dit is een groot pluspunt omdat praktisch enkel
 	horizontale krachten moeten opgevangen worden en de horizontale borging dus de belangrijkste
 	is.

-	Minder cognitieve belasting: als aan de gebruikers de mogelijkheid wordt gegeven om het
  product op eender welk punt in te stellen, is de kans groter dat hij/zij lang bezig zit aan
 	kleine tweaks om het “perfect” te krijgen, terwijl instelmogelijkheid constrainen tot enkele
 	punten ervoor zorgt dat de gebruiker slechts een van deze punten dient uit te kiezen en er
 	dan niet meer over hoeft te denken. 

*Dus ja, er wordt vrijheid van personalisatie ontnomen van de gebruiker, maar met voldoende klein genomen intervallen zouden alle gebruikers nog steeds een gepast instelpunt moeten kunnen vinden.*

-	Dit gaat verder op het vorige punt, irritaties zoals per ongeluk het stuk te ver verschuiven,
  zodat je de “sweet spot” weer terug moet gaan zoeken, worden grotendeels geëlimineerd met dit
 	systeem, aangezien het minder makkelijk per ongeluk verschuift door de zijwaartse borging,
 	maar ook omdat zo’n intervalpunt makkelijker terug te vinden is.

Het conceptueel behuizingstuk van het interval schuifsysteem: “Rail”, wordt in Figuur 10 weergegeven:



*Figuur 10: Conceptuele illustratie van het behuizingonderdeel van het schuifsysteem: “Rail”*

Zoals zichtbaar wordt gekozen voor een dubbele rij. Dit heeft als doelen extra zijwaartse borging toe te voegen, waardoor het sterker wordt en om het schuifstuk recht verticaal te houden.

De volgende stap is om te bepalen **wat** er verschuift wordt.

Hier zijn 2 opties:
    -	Bakjes verschuiven ten opzichte van elkaar
    -	Muren verschuiven ten opzichte van elkaar
Beide opties worden geanalyseerd op hun eigen voor- en nadelen:

---
###### 4.3.1.1 Bakjes Verschuiven

-	**Voordelen**
    * Minder cognitieve belasting en tijdsinname dan muurverschuiving, want minder te
      verschuiven onderdelen
    * Wordt beschouwd als een intuïtievere optie
    *  Minder complex
-	**Nadelen**
    * Vaste breedte van bakjes

---
###### 4.3.1.2 Muren verschuiven

-	**Voordelen**
    * Instelbare breedte van bakjes
-	**Nadelen**
    * Meer cognitieve belasting en tijdsinname dan muurverschuiving, want meer te verschuive,
      onderdelen
    * Wordt beschouwd als minder intuïtief
    * Complexer
    
Hier is 1 aspect zeer interessant: muurinstelling biedt de mogelijkheid om niet enkel de positie van voetplaatsing in te stellen, maar ook de breedte van de bakjes. Dit gaat dan wel ten koste van extra complexiteit en mogelijks een minder intuïtief geheel.

Dit is interessant, omdat in Deel I: Analyse van Voetafmetingen – Dimensionering van Bakje het grote verschil in voetgroottes binnen de groep leidt tot een zeer groot bakje voor relatief kleine voeten, bij een deel van de groep. Er is echter momenteel nog geen test uitgevoerd om te bepalen of dit effectief een probleem is of niet.

Een algemene zijwaartse denkroute toepasbaar op beide opties, is de vraag hoeveel stukken er verschoven worden.

Hier zijn ook twee mogelijkheden:

-	Alles verschuifbaar maken
    *	Bakjesverschuiving: 2 verschuifbare onderdelen
    *	Muurverschuiving: 4 verschuifbare onderdelen
-	1 stuk vastzetten aan de rail, welke dient als referentiepunt*
    *	Bakjesverschuiving: 1 verschuifbaar onderdeel
    *	Muurverschuiving: 3 verschuifbare onderdelen
    
Hierbij wordt gekozen voor de tweede optie: een vast referentiestuk integreren. Hiervoor geldt volgende redenering: het verhoogt intuïtiviteit en vermindert complexiteit, zowel qua onderdelen als het instelproces.

*_referentiepunt, bedoeld als zijnde vergelijkbaar met het opmeten met een schuifmaat: het ene uiteinde blijft vast, terwijl de meter kan verschoven worden._

---
###### 4.3.1.3 Beslissing van verschuifstuk

De muurinstelling biedt een volledige personalisatie aan de gebruiker. De breedte-instelling van de bakjes lijkt hoe dan ook een voordeel. Sommige gebruikers willen mogelijks een bakje dat ruimer zit, andere wat meer spannend. Dit zou er ook voor zorgen dat bij kleine voeten, de afstand tussen de bakjes onder de 130mm kan gebracht worden, wat de limiet van de vaste bakjes is (Figuur 4). 

Er wordt voor deze optie gekozen om verder te gaan in het proces, gebruikmakend van een referentiemuur.

Uit tests zal blijken of dit al dan niet te veel vrijheid biedt aan de gebruiker, de keuze van muurinstelling in plaats van bakjesinstelling niet voldoende intuïtief blijkt, of de referentiemuur het product makkelijk bruikbaar maakt en of ook dit intuïtief is.

---
##### 4.3.2 Vormbepaling en dimensionering
###### 4.3.2.1 Bodemplaat

Gezien besloten is dat de verschuifbare componenten muren worden in plaats van vaste bakjes, kunnen de bodems van de voorgaande bakjes nu samengevoegd worden tot één bodemplaat, waarover de muren zullen verschuiven.

---
###### 4.3.2.1.1 Breedte

De breedte ervan wordt bepaald door de maximale genomen instelafstand van de voorgaande bakjes te nemen (Figuur 7) en hierbij twee helften - oftewel één gehele – maximale voetbreedte bij op te tellen (Tabel 2):

*Tabel 2: Antropometrische gegevens van voetdimensies uit DINBelg*

| Populatiebeschrijving | Voetlengte (mm) | Voetbreedte (mm) |
|---|---:|---:|
| Mannen, 18-65, P99 | 289 | 114 |
| Meisjes, 6, P1 | 157 | 60 |

350 + 114 = **464mm**

---
###### 4.3.2.1.1 Lengte

De lengte wordt bepaald door de maximale voetlengte binnen de groep te nemen (Tabel 2).

Dit biedt het nadeel dat het minder compact is dan als bijvoorbeeld enkel de lengte van een bovenste helft van een voet genomen zou worden, maar er wordt hiervoor gekozen omwille van volgende redeneringen: 

-	Met een voet niet volledig op de plaat, zou de hiel stationair blijven tijdens de bediening
  van een knop langs deze kant. Dit zou aanleiding geven tot het meedraaien van het prototype
 	langs deze kant, welke dan ook voor een misinput langs de andere kant zou kunnen zorgen. Dit
 	wordt geschetst in Figuur 11:



*Figuur 11: Illustratie van geanticipeerd probleem dat zou kunnen optreden bij korte bodemplaat: verschuiving van product welke op zichzelf een annoyance is en mogelijks voor misinputs kan zorgen*

Het is de hoop dat als de volledige voet op de bodemplaat rust, in combinatie met goede grip onderaan de plaat, dit effect verminderd zou worden. Dit dient a.d.h.v. verdere tests gevalideerd te worden.

-	Het zou het product intuïtiever kunnen maken:
  Als de gebruiker voelt dat de muren met knoppen aan de rail vooraan hangen en er nog een plat
 	stuk vanachter is overgelaten, is het de hoop dat dit een extra indicatie geeft dat het de
 	bedoeling is om de voeten te plaatsen op de bodemplaat, elk binnen 2 muren, gericht naar de
 	rail.

-	Als de bodemplaat vervaardigd zou worden uit een comfortabel materiaal (wordt verder bepaald
  onder CMF), zou dit prototype met een plaat, waar de volledige voet op past, ook gebruikt
 	kunnen worden op harde/koude/ruwe/vuile… vloeren, terwijl de voeten volledig van de comfort
 	van de bodemplaat kunnen blijven genieten. 

Om het nadeel dat de plaat lomper en minder makkelijk transporteerbaar en opbergbaar zou worden als gevolg van deze gekozen lengte te verhelpen, zal deze opgedeeld worden in twee delen: een onderhelft en een bovenhelft.

Deze zal dan inklapbaar zijn (compacter en beter opbergbaar) en ook uitgerust worden met handvaten, waardoor de gebruiker deze in ingeklapte stand eenvoudig kan ronddragen.

De inklap- en ronddraagprincipes worden in Figuren 12 en 13 afgebeeld:



*Figuur 12: Illustratie van het inklapproces, doormiddel van gelijke verdeling van de bodemplaat in twee helften*



*Figuur 13: Illustratie van het draagproces, doormiddel van voorziene handvaten*

De lengte van het geheel is dus 289mm (twee helften van 144,5mm)(zie tabel 2)

*Deze dienen elk als richtwaarden. De maten dienen bij voorkeur niet lager dan deze waarden genomen te worden om te vermijden dat mensen worden buitengesloten (vooral bij de breedte) en ook niet onnodig veel groter omdat dit de compactheid vermindert, maar een lichte toename in functie van andere component(en) is toegelaten.*

---
###### 4.3.2.2 Rail (interval schuifsysteem)
###### 4.3.2.2.1 Vormbepaling

Achteraan de bodemplaat komt de rail terecht, met de inkeping/gleuf naar achteren gericht. Op deze manier kunnen de muren zich rond de rail klemmen.

Dit principe wordt geïllustreerd in Figuur 14:



*Figuur 14: Plaatsing van de rail, muur en bodemplaatcomponenten en contactpunten tussen de muur en de rail*

De verschuifbare muur beweegt door zijn geometrie vrij in de bovenste rijen. Dit is de schuifstand.

Wanneer de muur op een beschikbaar punt naar beneden geschoven wordt, is deze (met enige speling) horizontaal geborgd. Dit is de vaste stand.

Eens de vaste stand bereikt is, zijn er twee bouten voorzien die de gebruiker dient in te drukken. 

Eentje zit in de muur, aan de kant van de gleuf in de rail, zodanig dat bij indrukken de muur ook (met enige speling) verticaal geborgd is.

De andere zit aan het andere uiteinde van de muur, aan de kant van de gebruiker. Deze dient in het overeenstemmende voorziene gat in de bodemplaat geduwd te worden. Dit zorgt ervoor dat de muur niet (merkbaar) zijwaarts kan wiebelen aan dit uiteinde tijdens gebruik.

Op dit moment is de muur dus langs alle richtingen geborgd, van alle vrijheidsgraden ontnomen.

Het gehele schuif- en borgingsproces wordt in Figuur 15 afgebeeld en in Figuur 16 worden de twee borgingen meer gedetailleerd weergegeven:



*Figuur 15: Werkingsprincipe van het instelproces van de muur, waaronder verschuiving en borging*



*Figuur 16: Borgingsprincipes van het instelproces van de muur*

---
###### 4.3.2.2.2 Dimensionering
###### 4.3.2.2.2.1 Breedte van geheel

De breedte van de rail stemt overeen met de breedte van de bodemplaat. 
Deze bedraagt dus (voorlopig) 464mm.

---
###### 4.3.2.2.2.2 Breedtes van intervallen en tussenintervallen

Omdat zowel de gekozen voet-tot-voetafstand en de “bakjes”-breedte vrij te kiezen is, is het zinloos om hiervoor meer- en minder voorkomende instelpunten te bepalen om een variantie in hoeveelheid intervalpunten in zekere regio’s te voorzien.

In werkelijkheid zullen zo goed als alle punten over de gehele lengte wel door iemand binnen de groep gebruikt worden, behalve over de lengte van de minimale voetbreedte, genomen vanaf het referentiepunt, zie Figuur 14. Deze minimale voetbreedte bedraagt 60mm. (Tabel 2)



*Figuur 17: Ongebruikt deel van interval door de gekozen gebruikersgroep*

Binnenin dit interval geen borgingspunten voorzien in de rail en de bodemplaat, zou ook kunnen serveren als extra indicatie van hoe het product gebruikt moet worden. Het eerste punt waar de gebruiker de linkse verschuifbare muur zou kunnen vastzetten zou al een zekere ruimte overlaten tot de referentiemuur, waarbinnen 2 knoppen aan weerskanten beschikbaar staan, wat aan de gebruiker duidelijk kan maken dat hier de voet tussen zou moeten komen om de knoppen te bedienen. 

Hierdoor zou hij/zij hopelijk ook kunnen achterhalen dat de twee overblijvende verschuifbare muren dezelfde functie bieden, voor de andere voet.

Of dit effectief zo is, wordt duidelijk uit volgende tests.

Over de rest van de lengte van de rail zijn de instelpunten gelijkmatig verdeeld. Om de breedtes van de intervallen en tussenintervallen te bepalen, worden de doelen ervan overlopen.

  -	Genoeg instelopties bieden aan de gebruiker, maar niet overweldigend veel.
  -	Breedte van intervallen moet breed genoeg zijn om de muren te behuizen, zonder dat de
    instelpunten van de muren breken of losschieten bij horizontale kracht.
  -	Breedte van tussenintervallen moet breed en sterk genoeg zijn om de krachten van de muur op
    de rail op te vangen. 

Dit in rekening gehouden, wordt gekozen voor zowel een interval- als een tussenintervalbreedte van 5mm. Dit wordt weergegeven in Figuur 15:



*Figuur 18: Breedtes van intervallen en tussenintervallen*

---
###### 4.3.2.2.2.3 Dikte

De rail moet dik genoeg zijn om in de groefgedeeltes zowel de muur goed in te klemmen (mag niet loskomen) en ook met de overblijvende dikte nog sterk genoeg is. (Zie Figuur 14)

Met dit rekening houdend wordt gekozen voor een dikte van 15mm, met een gleufverhouding van 1/3, wat betekent dat de gleuf 5mm diep is en in de gleuf zo nog 10mm wand overblijft.
Dit wordt afgebeeld in Figuur 19:



*Figuur 19: Diktedimensies van de rail*

---
###### 4.3.2.2.2.4 Hoogte van het geheel

Voor de hoogte geldt hetzelfde principe als bij de breedtes van de intervallen en tussenintervallen, namelijk dat moet gekozen worden voor een maat die groot genoeg is om nog steeds voldoende sterk te zijn en de functionaliteiten te volbrengen, maar ook niet te groot, om compactheid te maximaliseren.

Hierbij gaat het om de volgende constraints:

-	Er moeten twee gleuven boven elkaar staan met genoeg ruimte tussen de gleuven zodat bij
  gebruik deze grens niet kan breken.
-	De gleuven zelf moeten een hoogte hebben, groot genoeg zodanig dat de stukken van de muur die
  erin komen (de klemmingsuitsteeksels, te zien in alle Figuren die de muren afbeelden) groot
 	genoeg kunnen zijn zodat deze niet breken bij gebruik en er een bout in kan passen die kan
 	ingeschoven worden bij de borging (zie Figuur 16, het eerste afgebeelde borgingsprincipe).

In functie van deze constraints, gecombineerd met de hoogte van de muren (4.3.2.3.2.2), wordt gekozen voor de dimensies afgebeeld in Figuur 20:



*Figuur 20: Hoogtedimensies van de rail*

---
###### 4.3.2.2.3 Gehele dimensionering van rail

Al de aparte designbeslissingen binnen de dimensionering van de rail leiden tot een allesomvattende dimensionering, waarvan de technische tekening in Figuur 21 afgebeeld staat.

Enkele opmerkingen:

-	De afstand waarover de gleuf is weggenomen uit de rail, is gereduceerd van 60mm
  (4.3.2.2.2.2.) tot 55mm aangezien de voornaamste functie ervan is om functionaliteit te
 	indiceren en op deze manier wordt vermeden dat onnodig mensen worden uitgesloten.

-	De breedte van de bodemplaat is verhoogd van 464mm (4.3.2.1.1.) naar 485mm, om de toegevoegde
  breedte door de muren (4.3.2.3.2.1.) op te vangen en ook zodat de gleuf eindigt op een
 	borgingspunt, waarbinnen bij instelling de grootste neutrale voet-tot-voetafstand alsook de
 	grootste voetbreedte kan bereikt worden.

-	De muur, vast inbegrepen aan de rail, volgt de dimensionering van de muren (4.3.2.3.), minus
  het klemstuk.

-	Aan elke verschuifbare muur is een behuizingsstuk voor de geïntegreerde drukknoppen
  (Schneider Electric Harmony Series Contact Block, 600V, 1 NO, zie Bill of Materials)



*Figuur 21: Gehele vormgeving en dimensionering van de rail*

---
###### 4.3.2.3 Muren
###### 4.3.2.3.1 Vormbepaling

De muren dienen de voeten op hun plek te houden, tegen een stoot te kunnen en verschuifbaar en borgbaar te zijn binnenin het schuifsysteem.

Dit leidt tot een algemene vorm zoals weergegeven in Figuur 14, met een klemvormig uiteinde welke over de rail loopt en zo in de gleuf terechtkomt.

De hoogte van het muurgedeelte moet groot genoeg zijn om tegen te houden dat de voet erover vliegt bij gebruik en er een knop van de gewenste grootte (4.3.2.5.) in kan geïntegreerd worden. 

De breedte moet groot genoeg zijn zodanig dat de borgingsstukken redelijk goed horizontaal geborgd blijven in de rail en zodanig dat de twee extra borgingsstaven erin geïntegreerd kunnen worden, welke dik genoeg zijn om niet te breken bij gebruik, zoals afgebeeld in Figuren 15 en 16. Ook moet de breedte groot genoeg zijn om voldoende schuifafstand te voorzien voor de knoppen (4.3.2.5.2.4.).

Zowel de hoogte als de breedte moeten groot genoeg zijn om voldoende kracht te kunnen opvangen.

---
###### 4.3.2.3.2 Dimensionering
###### 4.3.2.3.2.1 Breedtes

Voor de twee borgingsbouten wordt gekozen voor diameters van 5mm en 2,8mm, respectievelijk voor de verticale bout en de horizontale bout, aangezien de verticale bout meer kracht zal moeten opvangen omdat het het enige element is dat de muur vasthoudt aan die kant. 

In functie van toleranties worden de gaten voor deze bouten vergroot tot respectievelijk 5,1mm en 3mm.

Om genoeg wanddikte aan het verticale gat te voorzien (2,45mm), sterkte te bieden en voldoende schuifstand voor de knoppen te voorzien, wordt voor een muurbreedte van 10mm gekozen.

De breedtes van de klemstukjes aan de muur dienen ongeveer overeen te komen met de intervalbreedtes (4.3.2.2.2.2.), minus een speling/tolerantie van 0,2mm langs weerskanten, welke leidt tot een breedte van 4,6mm hiervoor.

Deze dimensies worden afgebeeld in Figuur 22: 



*Figuur 19: Breedtedimensies van de verschuifbare muren*

---
###### 4.3.2.3.2.2 Hoogtes

De hoogte wordt enerzijds bepaald door de knophoogte (4.3.2.5.2.2.), anderzijds in functie van het begrenzend vermogen dat het heeft voor de voeten.

Als referentie wordt de instaphoogte (“instep height”, aangeduid in Figuur 20) benaderd* voor het 99ste percentiel van mannen tussen de 18 en 65 jaar.

Volgende afmetingen zijn nodig (zie Figuur 23):
  -	Instaphoogte (Instep height, IH)
  -	Voetlengte – ter referentie (Foot length, FL)



*Figuur 23: Overzicht antropometrische gegevens van voetdimensies*

Deze gegevens worden verzameld uit een onderzoeksartikel, door Zhang et al.

* _Benaderd, aangezien niet-Belgische antropometrische gegevens worden gebruikt en doormiddel van verhouding tot voetlengte worden omgerekend naar de equivalent voor de grootste Belgische voeten (man, P99, 18-65 jaar)._

Als tweede bron van antropometrische gegevens wordt DINBelg geraadpleegd, met name de voetlengte van mannen, P99, 18-65 jaar. Zie Tabel 3:

*Tabel 3: Antropometrische gegevens van voetdimensies uit DINBelg*

| Populatiebeschrijving | Voetlengte (mm) |
|---|---:|
| Mannen, 18-65, P99 | 289 |

In Figuur 24 staan alle antropometrische metingen uit de gekozen bron.

Van elk van de dimensies wordt het gemiddelde en de standaarddeviatie gegeven, en voor elk ook de waarde bij:

  -	“NWB: Non-Weight Bearing”, voet zonder belasting (weinig tot geen contact met vloer)
  -	“HWB: Half Weight Bearing”, voet onder belasting van 50% lichaamsgewicht
  -	“80%WB: 80% Weight Bearing”, voet onder staande belasting
  -	
Voor deze toepassing is HWB de beste metriek, aangezien voor besturing de voet op de ondergrond wordt gedrukt in zekere mate, maar wel al zittend, dus niet met het volledige gewicht.



*Figuur 21: Antropometrische voetafmetingen bij verschillende belastingscondities, uit studie van Zhang et al. (2022)*

Volgende formule wordt voor de hierop volgende berekeningen gebruikt:

X_P = μ + Z_P * σ

XP: waarde van variabele bij percentiel P
μ: gemiddelde waarde
ZP: Z-score voor percentiel P
σ: standaarddeviatie

Ook volgende gegevens worden gebruikt (geëxtrapoleerd uit Figuur 25):
-	Z-score voor P1 = -2,3263
-	Z-score voor P99 = +2,3263



*Figuur 22: Z-score - percentieltabel voor normale distributie, uit Mathblog.com*

P99 = 58,5 + 2,3263 * 5,1 = 70,4mm

De verhouding van de instaphoogte t.o.v. de voetlengte wordt bepaald, waarna deze fractie vermenigvuldigd worden met de Belgische voetlengte (Tabel 4), om zo een schatting te maken van de waarde van de grootste voethoogte voor mannen uit België:

(70,36413/265,2) *289 = **76,68mm**

Dit gecombineerd met de hoogte van de knoppen, welke 19,5mm bedraagt (4.3.2.5.2.2.), maakt een muurhoogte van 30mm een veilige keuze. Het biedt ruim genoeg plaats om de knoppen in de muren te bergen en een verhouding van 30/76,68 is voldoende groot om de voeten zelfs bij harde tikken op hun plaats te houden (intuïtief, niet op basis van cijfers).

Dit houdt in dat er boven de knopholte nog 5mm overblijft. Deze waarde wordt behouden voor de hoogte/dikte van het klemstukgedeelte boven de rail en verdubbeld aan het klemstukgedeelte achter de rail, om meer gewicht aan deze kant te plaatsen (minder de neiging om te wiebelen of te bewegen) en ook om de horizontale borgingsstaaf goed te kunnen behuizen.

De borgingsstukken aan de klem volgen in hun hoogte dezelfde speling/tolerantie als bij de breedte ervan (4.3.2.3.2.1.) en hierdoor wordt ook voor hun hoogte voor 4,6mm gekozen. Op deze manier kan de muur in schuifstand soepel door de groeven bewegen, zonder dat deze klemstukken tegen de randen wrijven.

---
###### 4.3.2.3.2.3 Lengtes

De lengte van de muur dient lang genoeg te zijn om deze goed en stevig achteraan de rail te kunnen inklemmen, om de knoppen te kunnen behuizen en de voeten goed op hun plaats te kunnen houden.

Aangezien het idee is om de bodemplaat in twee helften op te delen, welke inklapbaar zal zijn op de manier afgebeeld in Figuren 15 en 16, wordt gekozen om de plaathelft aan de kant van de rail volledig te laten overspannen door de muren in lengterichting. Dit biedt namelijk het voordeel dat de afstand van de verticale borgingstaaf tot de borging aan de rail (Figuur 16) gemaximaliseerd wordt, wat ervoor zal zorgen dat de neiging voor de muren om te wiebelen bij bediening geminimaliseerd wordt. Kortom, dit biedt de beste algehele horizontale borging aan de muren.

De originele bodemplaatlengte bedroeg 289mm (4.3.2.1.2.), maar aangezien de rail 20mm dik zal zijn (4.3.2.2.2.3.), wordt deze dikte eraan toegevoegd en aangezien de voet niet altijd tot helemaal aan de rail zal rijken wordt deze nog verder tot 320mm verhoogd, welke twee helften van 160mm overhoudt. Hierdoor zal het “muurgedeelte” (minus klemgedeelte) ook 160mm bedragen.

Voor de lengte van het klemstukgedeelte achter de rail wordt een waarde van 15mm gekozen om meer gewicht aan deze kant te plaatsen (minder de neiging om te wiebelen of te bewegen) en ook om de horizontale borgingsstaaf goed te kunnen behuizen. Voor de lengte van het gehele klemstukgedeelte (boven en achter de rail) wordt hierbij nog de dikte van de rail  (15mm, zie Figuur 19) plus een speling van een millimeter toegevoegd, waaruit een totale lengte van 31mm bekomen wordt.

De lengte van de klemstukken zullen zoals in hun andere dimensies ook 4,6mm bedragen in functie van spelingruimte. Hierdoor zullen ook in deze richting de muren niet haperen en blijven hangen bij het instellen.

De dimensies van zowel de hoogtes en lengtes worden in Figuur 26 weergegeven:



*Figuur 26: Hoogte- en lengtedimensies van de verschuifbare muren*

---
###### 4.3.2.4 Bodemplaat - aanpassing

De dimensies van de bodemplaat worden aangepast als gevolg van de ontwerpkeuzes van de verschuifbare muren en de rail. De aanpassing van lengte is reeds toegelicht in 4.3.2.3.2.3., maar ook de breedte wordt aangepast. Deze was origineel 464mm (4.3.2.1.1.), maar moet vergroot worden naar een breedte die overeenstemt met de rail (4.3.2.2.3.). Dit verhoogt dus naar 485mm.

Deze nieuwe dimensies worden in Figuur 27 afgebeeld:



*Figuur 27: Nieuwe dimensies van de bodemplaat*

_Opmerking: de handvaten zijn nog niet bemaat, omdat de dimensies hiervan in de volgende- en laatste antropometrische analyse: Deel III: Analyse van Handafmetingen – Dimensionering van Handvat, zullen bepaald worden._

---
###### 4.3.2.5 knoppen
###### 4.3.2.5.1 Vormbepaling

De knoppen zullen een eenvoudige rechthoekige vorm hebben met een verticaal grippatroon, aangezien een complexere knopvorm overbodig is voor deze toepassing (enkel praktisch).

Voor het mechanisme wordt gekozen voor “een algemene/constante middelgrote indrukweerstand, waarbij je met een middelgrote weerstand de knop over een zekere afstand moet indrukken tot je het elektrisch contact bereikt en de input geregistreerd wordt.”, zie Figuur 28 en verdere uitleg in Deel I: Analyse van Voetafmetingen – Dimensionering van Bakje.



*Figuur 28: Keuze van de werkingsoptie voor de knoppen in functie van weerstandstoevoeging*

Hiervoor wordt gekozen omdat de Schneider Electric Harmony Series Contact Block, 600V, 1 NO drukknop die we gebruiken handig is in het opzicht van prototyping omdat je er eenvoudig kabels aan kan vast- en losmaken en deze ook zeer robuust is, wat noodzakelijk is bij voetbediening in deze gebruikscontext. Deze knop biedt de tweede opgelijste werkingsoptie in Figuur 28 niet als mogelijkheid, dus zal voor de externe knop een zeker schuifsysteem moeten geïntegreerd worden, binnenin de verschuifbare muur, welke acteert als een afstand die overbrugt moet worden tot je aan het effectief drukcontact terechtkomt.

---
###### 4.3.2.5.2 Dimensionering
###### 4.3.2.5.2.1 Lengte

De lengte van de knoppen is reeds bepaald in Deel I: Analyse van Voetafmetingen – Dimensionering van Bakje, namelijk een kleine knop van 30mm lang en een grote knop van 40mm lang per voet.

---
###### 4.3.2.5.2.2 Hoogte

De hoogte is nog onbepaald. Het belangrijkste hierbij is dat de knop niet ongemakkelijk aanvoelt aan de voet en vermeden wordt dat deze niet gemakkelijk meegaat bij induwen. Beide treden op bij een te kleine hoogte-tot-lengte verhouding. Echter mag hier ook niet in overdreven worden in functie van compactheid. Ook is deze afhankelijk van de gebruikte drukknop: Schneider Electric Harmony Series Contact Block, 600V, 1 NO.

Er wordt gekozen voor een hoogte van 20mm, omdat
-	20/76,68 = 0,26
->	Meer dan een kwart van de grootste voeten, zal niet ongemakkelijk aanvoelen

-	20/40 = 0,50
->	Deze hoogte-tot-lengte verhouding is voldoende zodanig dat deze makkelijk meegaat met het duwen

-	20 > 7,5
  7,5mm is de hoogte van het drukknopcontact, welke met ruime overschrijding bedekt zal worden
 	bij indrukking en een goed contact zou moeten garanderen.

---
###### 4.3.2.5.2.3 Dikte

De knop moet genoeg uitsteken om voelbaar en makkelijk bedienbaar te zijn. Hier wordt gekozen voor een dikte van 10mm, waarvan 7,7mm effectief uit de muur zal steken bij niet-ingedrukte stand.

---
###### 4.3.2.5.2.4 Mechanisme

Er wordt gekozen voor een inwendig schuifmechanisme binnenin de muren, op de manier zoals afgebeeld in Figuur 29:



*Figuur 29: Schuifmechanisme van de knoppen, geïntegreerd in de muren*

Hierdoor moet dus een uitsparing gelaten worden in de muren waarin de knop met een extra schuifstuk voortbeweegt. Voor dit schuifstuk wordt een hoogte van 9,8mm gekozen zodat deze er bij gebruik (muren op- en neer heffen), niet uitvallen. Deze zijn langs weerskanten 15mm lang om wiebelen van de knoppen te vermijden.

Er wordt bepaald hoever het drukknopcontact in de muur komt wanneer deze in de behuizing ligt zoals in Figuur 26. Dit is het punt waar de knop dient terecht te komen in “uit”-stand. De “in”-stand van de knop rijkt tot aan de rand van de drukknop, zodat bij bediening van de knop altijd een contact doorgegeven wordt.

Dit in rekening gebracht met het feit dat de muren 10mm zijn, constraint dit de dikte van het schuifstuk tot 1,8mm.

De dimensies relevant voor het schuifmechanisme worden in Figuur 30 weergegeven:



*Figuur 30: Dimensies voor het schuifmechanisme van de knoppen*

---
### 5 Conclusies
#### 5.1 Algemene conclusies

De benadering van de voet-tot-voetafstand varieert bij tussen 105mm en 340mm voor de gekozen extremumgroepen. 

De onnauwkeurigheid door de benadering wordt weggewerkt door beide verder in de richting van hun resp. extremum af te ronden:
-	Minimum: 105mm -> 100mm  
-	Maximum: 340 -> 350mm

Het origineel bakjesontwerp, bekomen in Deel I: Analyse van Voetafmetingen – Dimensionering van Bakje, wordt verworpen en in de plaats wordt verder gewerkt met een aaneengesloten, inklapbare bodemplaat met 4 muren. Zie Figuur 31:



*Figuur 31: Bekomen geïntegreerd ontwerp als resultaat van de beslissingen genomen in de analyse*

Deze dienen elk een kant van een voet te begrenzen en 3 van de 4 muren kunnen over de plaat verschoven worden (rode muren in Figuur 28). De overblijvende staat vast aan de rand en serveert als vast referentie-/meetpunt en reduceert de complexiteit.

Het verschuiven van de muren gaat via het “rail”-systeem, zoals weergegeven in Figuur 29:



*Figuur 32: Werkingsprincipe van het instelproces van de muur, waaronder verschuiving en borging*

Vastklemmen van de muren gebeurt door deze aan weerszijden te borgen, zoals weergegeven in Figuur 33:



*Figuur 33: Borgingsprincipes van het instelproces van de muur*

De inklapbaarheid van de bodemplaat biedt extra compactheid bij het opbergen, maar gecombineerd met handvaten aan weerskanten, zorgt het er ook voor dat zal kunnen gedragen worden zoals een koffer. De inklappings- en draagprincipes worden respectievelijk in Figuren 34 en 35 afgebeeld:



*Figuur 34: Illustratie van het inklapproces, doormiddel van gelijke verdeling van de bodemplaat in twee helften*



*Figuur 35: Illustratie van het draagproces, doormiddel van voorziene handvaten*

De dimensies van de handvaten dienen nog bepaald te worden in een volgende antropometrische analyse: Deel III: Analyse van Handafmetingen – Dimensionering van Handvat

De knoppen hebben een werkingsprincipe zoals geïllustreerd in Figuur 36:



*Figuur 36: Schuifmechanisme van de knoppen, geïntegreerd in de muren*

---
#### 5.2 Conclusies van Dimensionering
#### 5.2.1 Bodemplaat

De afmetingen van de bodemplaat zijn in Figuur 37 weergegeven:



*Figuur 34: Nieuwe dimensies van de bodemplaat*

De dikte is afhankelijk van de gebruikte houtplaat, aangezien het productieproces lasercutten zal zijn. Dit zal gebruikelijk 4mm bedragen.

---
#### 5.2.2 Rail

De afmetingen van de rail zijn in Figuur 38 weergegeven:



*Figuur 38: Gehele vormgeving en dimensionering van de rail*

De aanhangende muur volgt de dimensionering van de verschuifbare muren (4.3.2.3.2. of 5.2.3.) minus de klem.

---
#### 5.2.3 Muren

De afmetingen van de muren zijn in Figuur 39 weergegeven:



*Figuur 39: Gehele vormgeving en dimensionering van de muren*

---
#### 5.2.4 Knoppen

De afmetingen van de knoppen en hun mechanisme binnenin de muren zijn in Figuur 37 weergegeven:



*Figuur 40: Gehele vormgeving en dimensionering van de knoppen en hun schuifmechanisme*

---
### 6 Design requirements

- Om voor alle mensen binnen de doelgroep een comfortabele instelling te bieden voor voetplaatsing, is de bodemplaat 485mm lang. 

- Om alle mensen binnen de doelgroep hun voeten geheel op de bodemplaat te kunnen laten rusten, is de breedte ervan 320mm. 

- In functie van transport en compactheid wordt de bodemplaat in twee gelijke delen verdeeld, met een horizontale snijlijn, haaks op de lengte van de voet bij gebruik, welke de mogelijkheid biedt om het prototype in te klappen. 

- In functie van transport en compactheid worden aan weerszijden van het product handvatgaten voorzien, welke bij inklapping aligneren zodat ze samen als één handvat gebruikt kunnen worden om het product rond te dragen in ingeklapte stand. 

- Om zowel voldoende vrijheid van instelling voor de gebruikers, als voldoende stevigheid bij borging te bieden, worden de muren verschoven en vastgezet in een dubbel roostersysteem met zowel een borgings- als tussenborgingsafstand van 5mm. 

- Om voldoende stevigheid bij borging te bieden, heeft de behuizing van het dubbele rooster, de rail genoemd, een hoogte van 42 mm. 

- Om voldoende stevigheid bij borging te bieden, overbrugt het eerste rooster een afstand van 12mm tot 22mm, genomen vanaf de bodemplaat, in de behuizing van het dubbele rooster, de rail genoemd. Binnenin deze afstand is er een gelijke verdeling voor het borgings- en schuifstuk: respectievelijk 12mm tot 17mm en 17mm tot 22mm. 

- Om voldoende stevigheid bij borging te bieden, overbrugt het tweede rooster een afstand van 27mm tot 37mm, genomen vanaf de bodemplaat, in de behuizing van het dubbele rooster, de rail genoemd. Binnenin deze afstand is er een gelijke verdeling voor het borgings- en schuifstuk: respectievelijk 27mm tot 32mm en 32mm tot 37mm. 

- Om alle voeten binnen de doelgroep te behuizen en stoten ervan voldoende op te vangen, zijn er zijwaartse muren in de bakjes die elk 160mm uitsteken in lengte en een klemstuk van 31mm lang hebben. 

- Om complexiteit te verminderen en het geheel intuïtiever te maken komt één van de vier muren vast te staan aan de rail, helemaal links, vanuit het perspectief van de gebruiker. Deze muur is een “referentiemuur” en is een metafoor voor het vaste nulpunt van een schuifmaat of lat. 

- Om complexiteit te verminderen en het geheel intuïtiever te maken wordt de kant van de rail langs de zijde van de referentiemuur ontnomen van het dubbele rooster voor de eerste 55mm in de langsrichting, startend vanaf de uiterste zijkant van de referentiemuur. 

- Om de muren stevig te kunnen klemmen over de rail, krijgen ze elk (behalve de referentiemuur) een klemstuk die langs de voor-, boven-, en achterkant over de rail komt te staan, aan de voor- en bovenkant een hoogte van 5mm- en aan de achterkant een hoogte van 10mm heeft. De hoogte wordt telkens gemeten met de relevante zijkant van de rail als bodem genomen. De benamingen voor-, boven-, en zijkant zijn vanuit het perspectief van de gebruiker. 

- De “lepjes” van de knoppen, welke de knop behuizen en schuifbaar maken over het indrukinterval, dienen een hoogte van ongeveer 10mm te hebben, zodat bij het omhoogheffen van de muren om ze te verschuiven deze knoppen niet loskomen en mooi blijven zitten. 

- Om te vermijden dat de knop breekt en/of wiebelt bij indrukken, zijn deze “lepjes” langs weerskanten 15mm lang. 

- De knoppen dienen een vorm van textuur te hebben zodat dit grip biedt aan de voet bij gebruik. 

- Zodanig dat de knoppen niet te scherp/ongemakkelijk aanvoelen bij gebruik, krijgen deze een hoogte van 20mm. 

- Het indrukinterval van de knop bedraagt ongeveer 5mm, als balans tussen het vermijden van misinputs en het behouden van compactheid, stevigheid en de mogelijkheid om de inputs snel uit te kunnen voeren. 

- Voor stevigheid worden de muren bij vaststellen extra geborgd door een staaftje met een diameter van 3mm vanuit de muur door het bovenste rooster te duwen, wat verticale beweging van de muur blokkeert. 

- Voor stevigheid worden de muren bij vaststellen extra geborgd door een staaftje met een diameter van 5mm vanuit de muur door het overeenstemmende gat van de bodemplaat te duwen, helemaal vooraan de muur: het verst weg van de rail. Dit blokkeert horizontale beweging van de muur en hindert zo wiebelen ervan bij gebruik. 

- In functie van stevigheid heeft de rail een algehele dikte van 15mm, waarvan 10mm massief en 5mm met uitsnijdingen voor de roosters. 

---

### 7 Literatuurlijst
#### 7.1 Internetpagina's

DINBelg. (2005). DINBelg. https://www.dinbelg.be 

Zhang, L., Yick, K.-L., Li, P.-L., Yip, J., & Ng, S.-P. (2022). Foot deformation analysis with different load-bearing conditions to enhance diabetic footwear designs. PLOS ONE, 17(3), e0264233. https://doi.org/10.1371/journal.pone.0264233 

MathBlog. (2024, 7 maart). Z-score – Percentile table for normal distribution. https://mathblog.com/statistics/definitions/z-score/percentile-to-z-table/ 

---
#### 7.2 Boeken

Molenbroek, J., & de Bruin, R. (2005). Enhancing
the use of anthropometric data. Human Factors
in Design, Safety, and Management, 289-297.

---
#### 7.3 Generatieve AI

Generatieve AI (ChatGPT, OpenAI) is gebruikt ter ondersteuning bij het toepassen van APA-richtlijnen, waaronder het correct formatteren van bronvermeldingen en het verwijzen naar figuren en citaten. De output is gecontroleerd en waar nodig aangepast door de auteur.

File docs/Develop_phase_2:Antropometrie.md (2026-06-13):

# Develop 2 – Antropometrische Studie
## Deel I: Analyse van Voetafmetingen – Dimensionering van Bakje
### 1 Onderzoeksdoel

Het doel van dit onderzoek is om de dimensies van het bakje van een nieuwe prototype iteratie (Figuur 1) te definiëren. Het prototype moet voor beide voeten twee knoppen bieden, die indrukbaar zijn door de linkse en rechtse uiterste punten van de voet. Een visuele weergave van dit concept, alsook de te bepalen afmetingen, zijn weergegeven in Figuur 2. Deze onbekende dimensies worden bepaald doormiddel van een antropometrische analyse, gebruikmakend van bestaande betrouwbare antropometrische gegevens.



*Figuur 1: Theoretisch model waarvan de afmetingen in dit onderzoek gedefinieerd worden*



*Figuur 2: Weergave algemeen concept, gekende dimensies en te bepalen dimensies van theoretisch model*

---
### 2 Motivatie

Voor deze toepassing wordt een antropometrische analyse als noodzakelijk beschouwd, enerzijds omwille van het feit dat het onderzoeksproces zich in de tweede deelfase van de ontwikkelingsfase bevindt, waardoor van “quick and dirty” prototyping meer overgegaan moet worden tot iets degelijkere, beter uitgewerkte ontwerpiteraties. Anderzijds omwille van het feit dat de positie van deze twee knoppen en de nodige grootte ervan om door (bijna) alle voeten bruikbaar te kunnen zijn, zeer moeilijk intuïtief te bepalen is. Deze data is ook nog verder in het proces bruikbaar, in het geval dat niet met dit concept verdergegaan wordt.

---
### 3 Data

Als belangrijkste bron aan antropometrische gegevens wordt DINBelg gebruikt. 

Om de dimensies van de grootste reële voeten te bepalen, worden de beschikbare relevante gegevens van mannen, tussen de 18 en 65 jaar, binnen het 99ste percentiel (P99) geëxtrapoleerd.

Om de dimensies van de kleinste reële voeten te bepalen, worden de beschikbare relevante gegevens van meisjes, van 6 jaar, binnen het 1ste percentiel (P1) geëxtrapoleerd.

DINBelg biedt enkel voetlengte en voetbreedte als bruikbare gegevens. Deze zijn verzameld in Tabel 1:

*Tabel 1: Antropometrische gegevens van voetdimensies uit DINBelg*

| Populatiebeschrijving | Voetlengte (mm) | Voetbreedte (mm) |
|----------------------|-----------------|------------------|
| Mannen, 18-65, P99  | 289             | 114              |
| Meisjes, 6, P1      | 157             | 60               |

(Deze gegevens waren ook reeds toegepast bij de conceptweergave in Figuur 2)

Enkel deze gegevens bieden niet genoeg informatie om alle nodige afmetingen te bepalen. (Aangeduid met “?” in Figuur 2)

Volgende afmetingen zijn nog nodig (zie Figuur 3):
-	Ballengte (Ball length, BL)
-	Balbreedte (Ball width, BW)
-	Voetlengte – ter referentie (Foot length, FL)
-	Voetbreedte – ter referentie (Foot width, FW)



*Figuur 3: Overzicht antropometrische gegevens van voetdimensies*

Deze gegevens worden verzameld uit een onderzoeksartikel, door Zhang et al.

---
#### 3.1 Berekeningen

In Figuur 4 staan alle antropometrische metingen uit de gekozen bron.

Van elk van de dimensies wordt het gemiddelde en de standaarddeviatie gegeven, en voor elk ook de waarde bij:
-	“NWB: Non-Weight Bearing”, voet zonder belasting (weinig tot geen contact met vloer)
-	“HWB: Half Weight Bearing”, voet onder belasting van 50% lichaamsgewicht
-	“80%WB: 80% Weight Bearing”, voet onder staande belasting

Voor deze toepassing is HWB de beste metriek, aangezien voor besturing de voet op de ondergrond wordt gedrukt in zekere mate, maar wel al zittend, dus niet met het volledige gewicht.



*Figuur 4: Antropometrische voetafmetingen bij verschillende belastingscondities, uit studie van Zhang et al. (2022)*

Volgende formule wordt voor de hierop volgende berekeningen gebruikt:
X_P=μ+Z_P*σ
XP: waarde van variabele bij percentiel P
μ: gemiddelde waarde
ZP: Z-score voor percentiel P
σ: standaarddeviatie

Ook volgende gegevens worden gebruikt (geëxtrapoleerd uit Figuur 5):
-	Z-score voor P1 = -2,3263
-	Z-score voor P99 = +2,3263



*Figuur 5: Z-score - percentieltabel voor normale distributie, uit Mathblog.com*
  
---
##### 3.1.1 Ballengte

_Mannen_

P99=182,6+2,3263*6,9=198,7mm

_Vrouwen_

P1=171,8-2,3263*8,0=153,2mm

---
##### 3.1.2 Balbreedte

_Mannen_

P99=96,9+2,3263*5,8=110,4mm

_Vrouwen_

P1=93,5-2,3263*6,2=79,1mm

---
##### 3.1.3 Voetlengte

_Mannen_

P99=246,1+2,3263*8,2=265,2mm

_Vrouwen_

P1=243,3-2,3263*10,1=219,8mm

---
##### 3.1.4 Voetbreedte

_Mannen_

P99=93,8+2,3263*5,9=107,5mm

_Vrouwen_

P1=90,7-2,3263*6,1=76,5mm

Deze gegevens zijn verzameld in Tabel 2:

*Tabel 2: Relevante percentielen uit antropometrische gegevens van Figuur 4*

| Populatiebeschrijving                          | Ballengte (mm) | Balbreedte (mm) | Voetlengte (mm) | Voetbreedte (mm) |
|------------------------------------------------|----------------|-----------------|-----------------|------------------|
| *Mannen, 66 ± 4 (60–72) jaar, P99*             | 198,7          | 110,4           | 265,2           | 107,5            |
| *Vrouwen, 64 ± 5 (56–75) jaar, P1*             | 153,2          | 79,1            | 219,8           | 76,5             |

De verhouding van de ballengte t.o.v. de voetlengte wordt bepaald voor zowel mannen als vrouwen, waarna deze fractie vermenigvuldigd worden met de Belgische voetlengte gegevens (Tabel 1), om zo een schatting te maken van de waarden van ballengtes voor mannen en vrouwen uit België:

_Mannen_

(198,7/265,2)*289=216,5mm

_Vrouwen_

(153,2/219,8)*157=109,4mm

Uit de balbreedte en voetbreedte kan de cosinus van de hoek tussen D4 en D5 (Figuur 3) en zo ook de hoek zelf bepaald worden, welke door combinatie met Belgische voetbreedte gegevens uit DINBelg gebruikt kunnen worden om de verticale afstand tussen de twee extrema van voetbreedtepunten in België te schatten. Ook dit gebeurt voor zowel mannen als vrouwen:

_Mannen_

sin⁡(cos^(-1)⁡〖107,5/110,4〗 )*114=25,8mm

_Vrouwen_

sin⁡(cos^(-1)⁡〖76,5/79,1〗 )*60=15,2mm

Alle relevante Belgische gegevens en schattingen worden verzameld in Tabel 3:

*Tabel 3: Belgische antropometrische gegevens en schattingen voor voetafmetingen, relevant voor dimensiebepaling binnen het concept*

| Populatiebeschrijving      | Ballengte (mm) | Verticale afstand tussen maximale breedtepunten v/d voet (mm) | Voetlengte (mm) | Voetbreedte (mm) |
|----------------------------|----------------|----------------------------------------------------------------|-----------------|------------------|
| *Mannen, 18-65, P99*       | 216,5*         | 25,8*                                                         | 289             | 114              |
| *Meisjes, 6, P1*           | 109,4*         | 15,2*                                                         | 157             | 60               |

*(Schattingen van waarden, niet werkelijk gemeten)*

**Opmerking**

De vermenging van vrouwelijke kindergegevens met volwassen gegevens leidt tot een zekere graad van onnauwkeurigheid. Deze berekening is een schatting. Ook deze tussen volwassen mannen is minder betrouwbaar dan werkelijke antropometrische metingen.

Om deze onnauwkeurigheden op te vangen wordt genoeg marge genomen bij de dimensies van het uit te werken concept.

---
### 4 Data analyse

Het is de bedoeling dat de voet tot helemaal achteraan in het bakje geplaatst wordt bij gebruik (zie Figuur 2), dus voor de dimensiebepaling wordt van bovenuit gerekend. Ook zoals te zien in Figuur 2 (blauw aangeduid) en zoals als nodig gevonden bij de berekeningen (zie 4.1.: Opmerking), zal op de aangeduide plaatsen een zekere extra uitsparing voorzien worden.

---
#### 4.1 Minimale en maximale maten, zonder toegevoegde marges

Met behulp van de waarden uit Tabel 3, kunnen binnenin het theoretische bakje al de aanrakingspunten aangeduid worden van de maximale breedtepunten van de voet, van zowel de grootste mannelijke voet, als de kleinste vrouwelijke voet. Deze zijn de punten op de voet die contact moeten maken met de drukknoppen (zie Figuur 2). 

Deze contactpunten zijn de extrema langs beide kanten, dus vormen ook de theoretische range, zonder toegevoegde marges, waartussen contacten van zo goed als alle soorten voeten kunnen liggen, als de tip van de voet het einde van het bakje raakt zoals bedoeld.

De grafische combinatie van gegevens uit Tabel 3 worden gevisualiseerd in Figuur 6. De bekomen contactrange als gevolg, wordt gevisualiseerd in Figuur 7:



*Figuur 6: Grafische voorstelling van antropometrische gegevens van voetafmetingen, uit Tabel 3*



*Figuur 7: Contact-/Inputranges bekomen uit antropometrische gegevens van voetafmetingen uit Tabel 3*

---
#### 4.2 Marge toevoeging aan contactranges

Aangezien er voor deze schattingen geen manier is om de “mate van onnauwkeurigheid” eenduidig te bepalen, wordt voor elke range een arbitraire, grotere maat gekozen.

Beide maten worden met ~5mm vergroot:
-	24,9mm -> 30mm
-	35,5mm -> 40mm
---
#### 4.3 Hoogtebepaling

Aangezien de maximale breedtepunten van de voet tot zeer laag richting de voetzool lopen met een quasi constante uitwijking, is de hoogte waarop het contact (knop) ligt een factor die vrij te kiezen is, grotendeels onafhankelijk van antropometrie. Hierbij wordt dan rekening gehouden met volgende factoren

-	Compactheid: Hoe minder hoog, hoe beter, voor bergbaarheid, combinatiemogelijkheid met piano pedalen,
  gewicht, etc., zolang dit niet (te veel) ten koste gaat van een andere belangrijke requirement.

-	Comfort: Aangezien de knop waarschijnlijk een grote weerstand zal hebben, om verkeerde inputs te vermijden,
  zou een zeer dunne, lange knop bij langdurig gebruik tot last kunnen leiden. Een dikkere knop is dus beter.

-	Containment: Als de rand te laag ligt, kan het optreden dat de voet niet goed genoeg begrensd wordt, waardoor
  die er bij gebruik uit kan vliegen.

Rekening houdend met deze factoren, wordt voorlopig voor een wandhoogte van 3cm gekozen, met knoppen die 2cm hoog zijn, startend vanaf de basis.

---
#### 4.4 Dimensionering van concept

Alle gezochte maten van dit onderzoek zijn bepaald, welke tot een eerste volledig gedimensioneerd concept leiden.

Dit wordt afgebeeld in Figuur 8:



*Figuur 8: Voorlopig finaal gedimensioneerd concept*

**Opmerking**

Dit is slechts een veralgemeende voorstelling. Zaken als bedrading, behuizing voor elektronica, etc., worden beïnvloed door onder andere technische specificaties en vallen buiten de scope van dit onderzoek.

---
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

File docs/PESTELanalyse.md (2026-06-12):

# Develop 3 – Pestel analyse
# 1 Onderzoeksdoel

De verkregen feedback van studenten kennismaatschappij en ICT, geformuleerd vanuit een PESTEL* analyse analyseren en hieruit implicaties op ons ontwerp afleiden.

_*PESTEL analyse: een kader dat kijkt naar Politieke, Economische, Sociale, Technologische, Ecologische en Legale factoren._

___
# 2 Motivatie

Deze analyse kan leiden tot nuttige nieuwe inzichten en mogelijke zaken die tot nog toe over het hoofd werden gezien binnen ons ontwerpproces, welke bij toepassing een positieve invloed zou kunnen hebben.

___
# 3 Analyse
## 3.1 Politiek
#### 3.1.1 Feedback van studenten

Wat volgt is een geparafraseerde transcriptie van de feedbackvideo op politiek vlak:

_Hebben jullie al nagedacht of jullie product in aanmerking zou komen voor overheidssubsidies of steun van toegankelijkheidsorganisaties?_

_Niet enkel interessant vanuit zakelijk perspectief, maar het geeft jullie product ook meer legitimiteit: als een overheid bereid is het product te steunen, betekent dat dat er een echte maatschappelijke nood is._

_Advies: hierover al eens nadenken._

___
#### 3.1.2 Huidige situatie

Hier is nog niet al te diep op ingegaan voorlopig, buiten het idee dat we zouden kunnen samenwerken met muziekscholen.

___
#### 3.1.3 Reflectie

Dit ligt momenteel niet prioritair. De prioriteit is eerst om het product conceptueel in orde te krijgen. Dit zal als spreekonderwerp geïntegreerd worden binnen de QAP* van volgende gebruikerstests, maar een grondig onderzoek hiervan zal eerder voor later zijn.

_*QAP: Question Asking Protocol_

___
## 3.2 Economisch
#### 3.2.1 Feedback van studenten

Wat volgt is een geparafraseerde transcriptie van de feedbackvideo op economisch vlak:

_Jullie verkregen het ontwerpinzicht dat het product stevig en robuust moest zijn in gebruikerstest 1._

_Maar, stevigere materialen kosten meer geld, wat leidt tot een spanningsveld._

_Het product te duur maken kan juist de mensen die het nodig hebben uitsluiten, aangezien mensen met een visuele beperking gemiddeld een lagere arbeidsmarktparticipatie hebben, wat financiële drempels extra pijnlijk maakt._

_Advies: tijdens volgende interviews naar mensen pijlen wat ze bereid zouden zijn te betalen voor een afgewerkte en robuuste versie van het product -> reële en economische haalbaarheid._

___
#### 3.2.2 Huidige situatie

In gebruikerstest 2 van Develop 2 werd hier al naar gevraagd, alsook een algemeen gesprek over CMF.

De bekomen inzichten waren:

De bekomen inzichten waren:
-	De proefpersoon zou bereid zijn om €300 te betalen voor een afgewerkt product.
-	De proefpersoon is van mening dat de prijs die iemand zou willen betalen meer afhangt van noodzaak dan van inkomen, algemeen gezien.

Bijgevolge dit een inzicht is uit een enkel interview (N = 1), dient deze informatie met een korrel zout genomen te worden.

___
#### 3.2.3 Reflectie

Bij de komende gebruikerstests zal er in de QAP’s blijven gepeild worden naar de prijs die hij/zij bereid zou zijn om te betalen en nog verdere algemene economische vragen, zoals wat hij/zij vindt van de prijzen van huidige hulpmiddelen en hoe de trend momenteel is van soorten middelen die (gedeeltelijke) overheidstussenkomst krijgen (valt samen met 4.1. Politiek)

Algemeen gezien zal het voor ons in ieder geval het doel zijn om de gewenste functionaliteit, gevoel van robuustheid, contrast, textuur, ... te bereiken aan een zo laag mogelijke kostprijs.

___
## 3.3 Sociaal
#### 3.3.1 Feedback van studenten

Wat volgt is een geparafraseerde transcriptie van de feedbackvideo op sociaal vlak:

_Een van de grote problemen voor slechtzienden en blinden dat jullie beschrijven is de hoge cognitieve drempel om braille partituren te lezen. Het doel van jullie product is deze drempel te verlagen en dat is het goede uitgangspunt._

_Maar, de bediening via de pedalen kan mogelijks zelf een nieuwe cognitieve drempel vormen. Als een muzikant moet onthouden welke pedaal overeenkomt met welke actie, naast al het andere dat hij of zij al in gedachten houdt tijdens het musiceren, kan dat overweldigend worden._

_Advies: zeer sterk focussen op de balans tussen functionaliteit en eenvoud. Minder is soms meer. Niet enkel testen of de gebruiker het product begrijpt, maar ook of het aanvoelt als een verlichting of een extra last._

___
#### 3.3.2 Huidige situatie

Er is al nagedacht om het product in te stellen in een “basismodus” en “gevorderde modus”. Bij vorige prototypes uitte dit zich onder de vorm van een toe te voegen inputcomponent welke de geavanceerde functies biedt, maar met de huidige ontwerpvisie zou het gaan om eenzelfde product, waarvan je de moeilijkere functies: switchen en loopen, uit zou kunnen zetten zodat gebruik eenvoudiger is. Dit zou in te stellen kunnen zijn binnen de app, of een knop aan het prototype, daar zijn we nog niet over uit.

___
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

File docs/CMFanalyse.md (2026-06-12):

# Develop 3 – CMF analyse
## 1 Onderzoeksdoel

Het doel van dit onderzoek is om via een CMF-analyse te bepalen welke kleuren, materialen en afwerkingen het meest geschikt zijn voor de side buttons voor blinde en slechtziende gebruikers. Het product moet gebruikers toelaten om audio-partituren intuïtief te bedienen door met de voeten tikken te geven op verschillende knoppen. Daarom wordt onderzocht hoe tactiele verschillen, antislipmaterialen, duidelijke contrasten en duurzame afwerkingen kunnen bijdragen
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

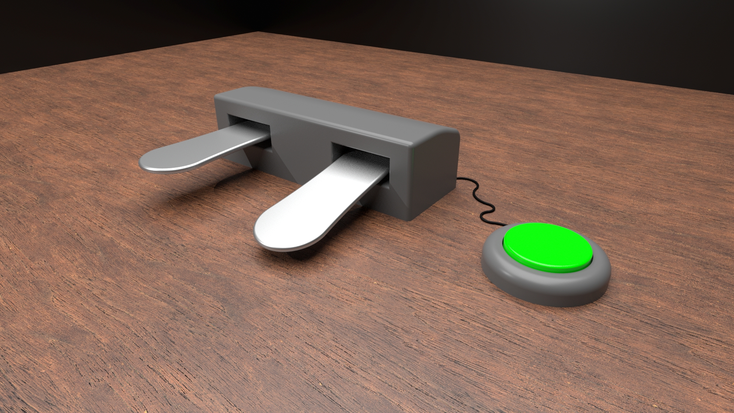
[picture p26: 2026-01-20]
Proofofconcept.jpg

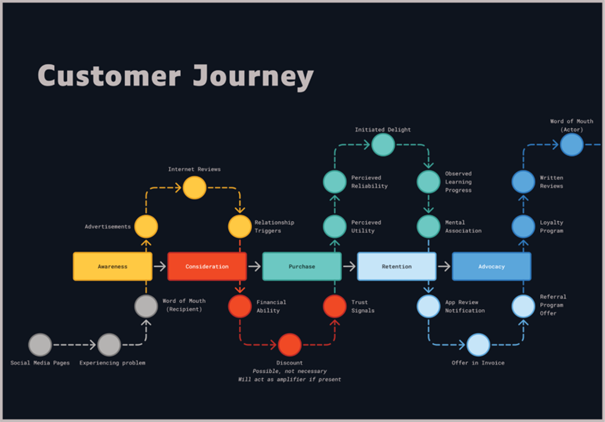
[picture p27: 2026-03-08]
img/DEV7.png

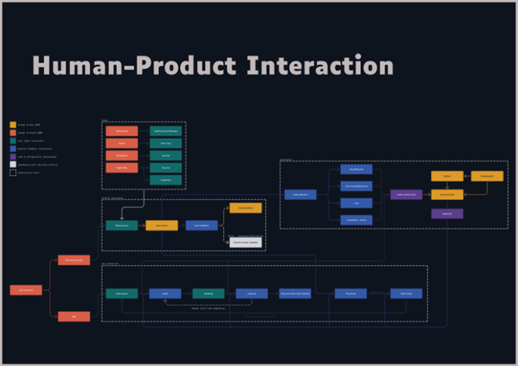
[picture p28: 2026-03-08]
img/DEV3.png

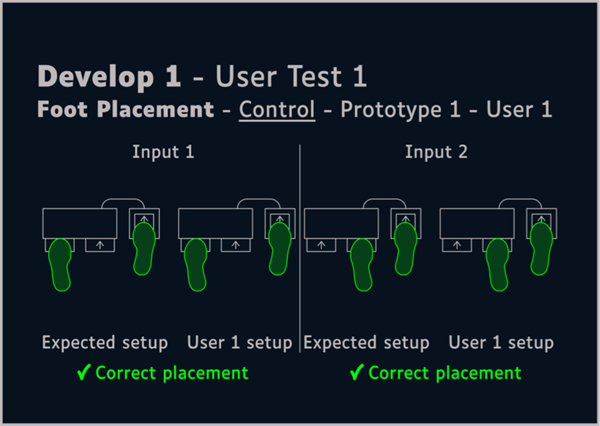
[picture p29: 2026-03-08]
img/RES7.png

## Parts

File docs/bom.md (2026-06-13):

## Bill of materials
| <u>**Wat**</u> | Link | Prijs (euro) |
|---|---|---|
| Anti-slip meubelpads | [Link 1](https://www.action.com/nl-be/p/3215822/anti-slip-meubelpads/) | 0,99 |
|---|---|---|
| <u>**Electronics**</u> |  |  |
| Schneider Electric Harmony XAL Series Contact Block | [Link 2](https://nl.rs-online.com/web/p/push-button-contact-blocks-light-blocks/3310574) | 7,47 |
| ESP32 | [Link 3](https://nl.aliexpress.com/item/1005006458998450.html?spm=a2g0o.order_list.order_list_main.5.2a2c79d2Uctu03&gatewayAdapt=glo2nld) | 4,79 |
| 3 Watt speaker | [Link 4](https://nl.aliexpress.com/item/1005008025171023.html?spm=a2g0o.order_list.order_list_main.24.2a2c79d2Uctu03&gatewayAdapt=glo2nld) | 2,75 |
| DFPlayer mini | [Link 6](https://nl.aliexpress.com/item/1005008209885534.html?spm=a2g0o.order_list.order_list_main.30.2a2c79d2Uctu03&gatewayAdapt=glo2nld) | 2,13 |
| Breadboard | [Link 7](https://www.kiwi-electronics.com/nl/400-punt-breadboard-wit-283?country=BE&gad_source=1&gad_campaignid=19763236734&gclid=Cj0KCQjw_7PRBhDcARIsAMjV7jnmotBbvo4oJwZ_MgTGvO2z2zTF6wP1MVB3DD4XwPFDEkTv6m7hWWcaAsYFEALw_wcB) | 3,62 |
| Wagos | [Link 8](https://www.brico.be/nl/elektra/bedrading/kabelverbinders-kabeldozen/verbindingsklemmen-elektriciteit/wago-verbindingsklem-hersluitbaar-dubbel-0-2-4-0-mm2-oranje-6-stuks/10105408) | 6,20 |
| Boxdraad | [Link 9](https://www.amazon.com.be/-/nl/luidsprekerkabel-elektrische-koperdraad-bedrading-doe-het-zelfprojecten/dp/B0FC28MZSR/ref=asc_df_B0FC28MZSR?mcid=52b1d6c16c333b0b83c60957c34e765d&tag=begogshpadd0d-21&linkCode=df0&hvadid=740696233156&hvpos=&hvnetw=g&hvrand=9595553950675008988&hvpone=&hvptwo=&hvqmt=&hvdev=c&hvdvcmdl=&hvlocint=&hvlocphy=1001278&hvtargid=pla-2441744731113&psc=1&language=nl_BE&gad_source=1) | 5,99 |
|---|---|---|
| <u>**Materials**</u> |  |  |
| PLA (3D print filament) 633 gr | [Link 10](https://eu.elegoo.com/products/pla-filament-1-75mm-colored-1kg?variant=gid://shopify/ProductVariant/51888865837332&gad_source=1&gad_campaignid=23872839547&gclid=Cj0KCQjw_7PRBhDcARIsAMjV7jkYPE1CJOypTnMBtF_swxUjDNLibHnnH5JfK7WFK0WP_5VpCQrZCZoaAi7jEALw_wcB) | 8,23 |
| Multiplex | IDC | 8,00 |

__Totaal = 50,17 Euro__

## Stappenplan
Voor het zelfstandig bouwen van dit prototype kunnen de fasen opgesplitst worden in de behuizing en elektronica.

__Behuizing:__

- Alle nodige files voor het 3D printen en laser cutten zijn in [docs/Prototyping](./Prototyping/) te vinden.

- Eerst wordt de multiplex plaat gelasercut volgens de DXF file. 

- Vervolgens worden alle onderdelen geprint. 

- Beide rail onderdelen en de linkse muur worden in elkaar geklikt en via de onderkant aan de plaat geboord. 

- Vervolgens worden de muurtjes één voor één op de rail geschoven tot ze op de passende plaats zitten voor de voet. 

- Waneer de muurtjes nu worden opgetilt kunnen de knoppen er worden ondergeschoven. 

- Vervolgens kunnen de muren weer naar beneden en vast gezet worden met de witte pinnen aan de achterkant. 

- Vervolgens kunnen de schakelaars in de behuizing gelegt worden en de kabels verbonden worden met behulp van een schroevendraaier. 

- De laatste stap voor de behuizing is de houder voor de elektronica, deze wordt met een bout links de linker muur bevestigd.

__Elektronica:__

Voor het elektronica gedeelde staat alles beschreven in deze [pagina](https://github.com/MatteaClaeys/Opkomende_Tech_MC_KH)

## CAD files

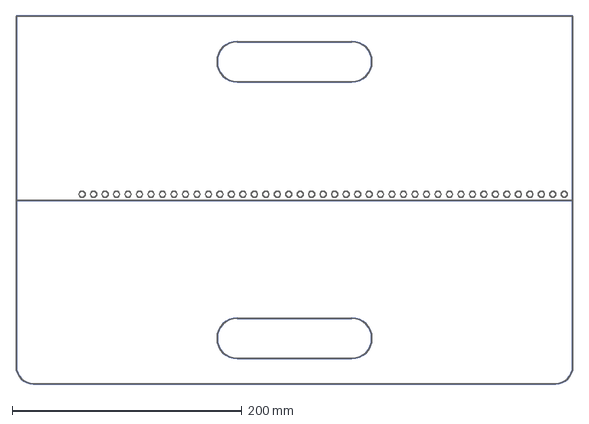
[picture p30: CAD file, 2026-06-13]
docs/Prototyping/Bodemplaat.dxf
485.0 x 320.0 mm

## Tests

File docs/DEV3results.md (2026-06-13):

# Develop 3 – Resultaten

Voor de volledige rapportering zie (Bijlagen Develop 3: rapport). Deze testen werden uitgevoerd op basis van het protocol (Bijlagen Develop 3: Protocol)

## 1 Functie/Gebruiks test
### 1.1 Functie test

Het prototype werd aan de gebruiker gegeven en er werd gevraagd om deze op de grond te plaatsen in de gebruiksplaatsing. Vervolgens werden auditief de functies per input meegedeeld als een soort van auditieve tutorial (de lay-out van de knoppen is te zien in figuur 1).

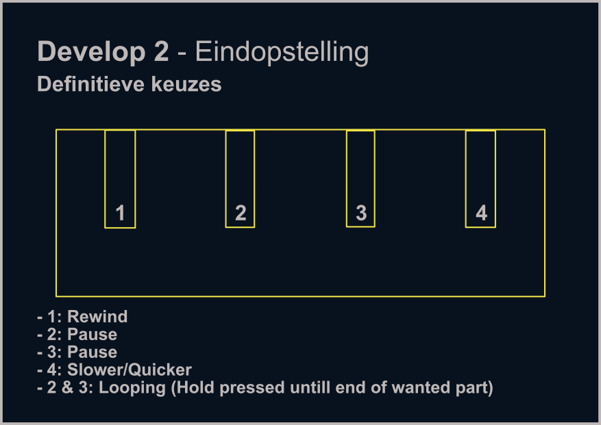
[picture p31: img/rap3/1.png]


Kwantitatieve resultaten van beide testen:

-	Test 1
1.	Speel: FOUT -> OK
2.	Pauzeer, Speel: OK, OK
3.	Looping aan: FOUT -> OK
4.	Looping uit: OK
5.	Versnellen: OK
6.	Vertragen: OK
7.	Resetten: OK
8.	Uitzetten (pauzeer): OK

-	Test 2
1.	Speel: FOUT -> OK
2.	Pauzeer, Speel: OK, OK
3.	Looping aan: OK
4.	Looping uit: OK
5.	Versnellen: OK
6.	Vertragen: OK
7.	Resetten: DEFECT
8.	Uitzetten (pauzeer): OK

Belangrijkste resultaatspunten:

-	Inputs van functies werden door beide personen als comfortabel ervaren, zowel met als zonder schoenen.
-	Er was één merkbare hapering tijdens de test, namelijk het wachten tot een teken dat de looping gestart of gestopt was.
-	De systeemcode beperkt het maken van misinputs, voor zover deze twee testen hebben kunnen aantonen.
-	De lay-out werd beschreven als intuïtief.
-	De loop functie heeft een soort feedback nodig welke aantoont dat de looping start en/of bezig is.

---

### 1.2 Gebruikstest

Nu werd de gebruiker gevraagd om aan hun instrument te zitten of hun instrument bij de hand te nemen. Wegens tijdlimieten kon deze test maar door één respondent uitgevoerd worden. Er werd simpelweg gevraagd aan de gebruiker om het product te gebruiken met als doel het stukje muziek na te kunnen spelen. 

Belangrijkste punten:
-	De handen konden op het instrument blijven gedurende de hele test.
-	Bediening gebeurde spontaan.
-	De gebruiker was erin geslaagd om het stuk (complexe) muziek vrij snel in zekere mate te leren (belangrijk hierbij is dat de proefpersoon een ervaren muzikant is, dit resultaat is dus niet representatief voor de “gemiddelde” muzikant).
-	Er is nood aan een door- en terugspoel functie.
-	Het testresultaat werd deels beïnvloed door stress.

---

## 2 CMF/APP (QAP)

In dit interview werd er bij de testpersonen gepolst naar antwoorden op vragen in verband met materiaalkeuzes, kleuren en finishes. Hierbij kan een toekomstige versie van het prototype nog toegankelijker zijn voor de doel groep. Ook werden er vragen gesteld in verband met de app. Deze vragen gaan vooral over data verzameling en accounts. (De vragen/antwoorden lijst staat in het rapport)

Belangrijkste punten:
-	Men heeft over het algemeen een iets terughoudendere kijk op accounts. Men heeft er een voorkeur voor dat accounts weggelaten worden als deze niet noodzakelijk zijn voor de app.

-	Er is geen consensus over hoe de bodemplaat zou moeten aanvoelen. Verder CMF-onderzoek zal hierop antwoord moeten bieden.

-	Buiten de bodemplaat maakt het beide interviewees niet zoveel uit hoe de resterende onderdelen aanvoelen. Men legt de focus vooral op kostenbesparing. -> Geen onnodig dure materialen.

-	Beide hebben of als laatste of helemaal niet de bodemplaat als onderdeel opgenoemd. Dit toont aan dat onze poging om de bodemplaat vorm te geven die duidelijk uitstraalt dat het buiten ondergrond geen functie heeft bij het bedienen, gelukt is. Dit vermindert de cognitieve lading van het product.

-	Er is geen duidelijke consensus over de mening van het delen van gegevens. Eén persoon gaf aan hier zorgvuldig mee om te gaan, dus het is algemeen de ethisch correcte keuze om in het geval een account gebruikt dient te worden, gegevens lokaal op te slaan, niet in een cloud/database en ook enkel de absoluut nodige gegevens op te slaan.

-	Een tutorial binnen de app zou een grote meerwaarde bieden om met het product te leren werken volgens de interviewees. Op intuïtieve basis zijn wij het hier ook mee eens. Deze wordt het best geïntegreerd in de app, op een intuïtieve en snel regelbare manier. (Binnen het “Settings”-menu)

-	Ook het idee om het product te kunnen regelen tussen een “basisversie” en “gevorderde versie” werd positief ontvangen.
Dit lijkt voor ons ook een idee dat een voordeel zou bieden voor het leerproces, mogelijks zelfs onder de vorm van het zelf aanduiden van welke functies je al dan niet actief zet. Als dit geen te grote cognitieve lading met zich meeneemt, is het volledig aan de gebruiker om te kiezen welke functies hij/zij wel of niet wil, wat een optimale persoonlijke gebruikservaring zou kunnen bieden.

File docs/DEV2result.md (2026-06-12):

# Develop 2 – Prototype resultaat

Met de twee ontworpen prototypes werden (N=2) testen uitgevoerd. Hier zal besproken worden wat de resultaten van deze testen waren. Indien de volledige raportering gewenst is, open dan de link op de hoofd pagina (Develop 2 - rapport).

## 1 Semi-functionele prototype

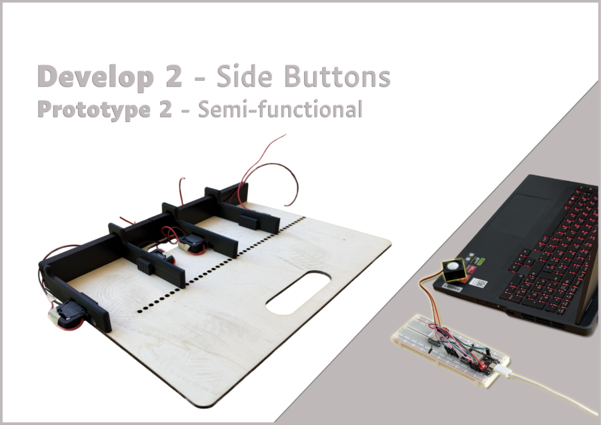
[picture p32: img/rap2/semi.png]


Voor deze test werd gevraagd aan de test persona om het prototype correct op te stellen op de grond. hierbij werd gekeken naar hoe het op de grond staat, maar vooral hoe het georiënteerd staat. Vervolgens wordt gevraagd aan de gebruiker om de voeten te plaatsen zoals het product moet gebruikt worden volgens hen. Hier wordt vooral gekeken of het instellen intuïtief is en of the voeten juist georiëntieerd staan. In onderstaande foto's staan de te verwachte resultaten.

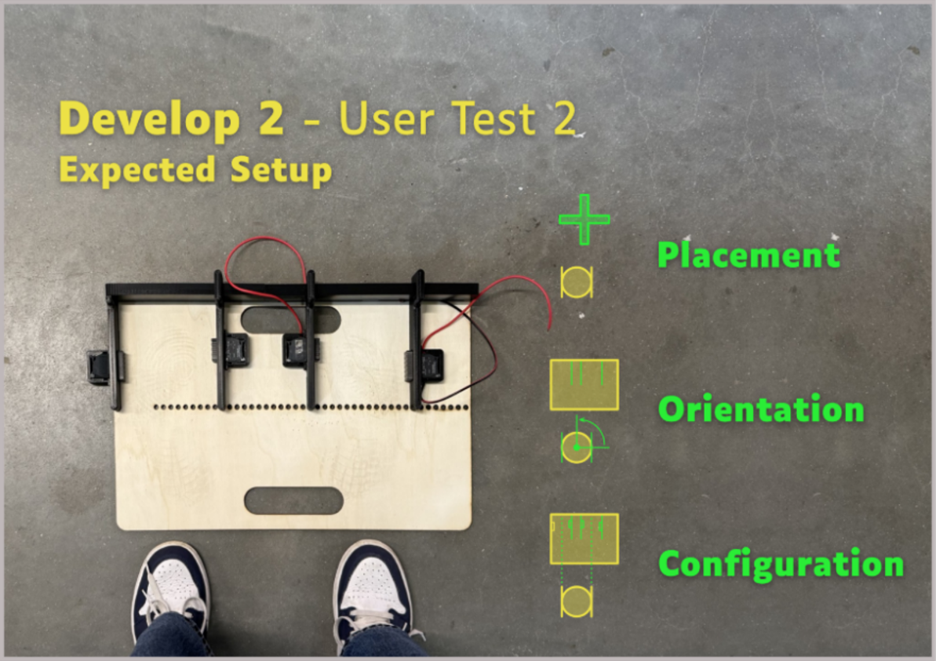
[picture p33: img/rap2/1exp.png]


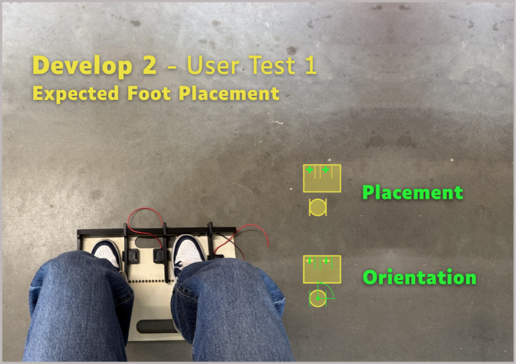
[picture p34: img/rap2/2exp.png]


### a. Test 1

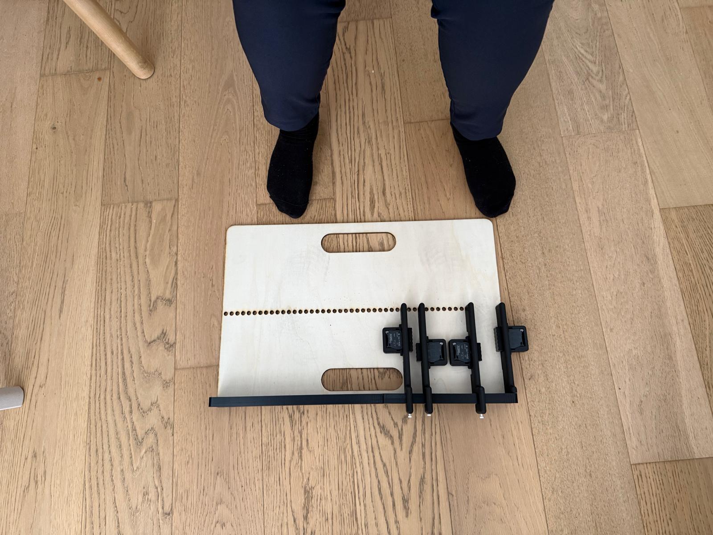
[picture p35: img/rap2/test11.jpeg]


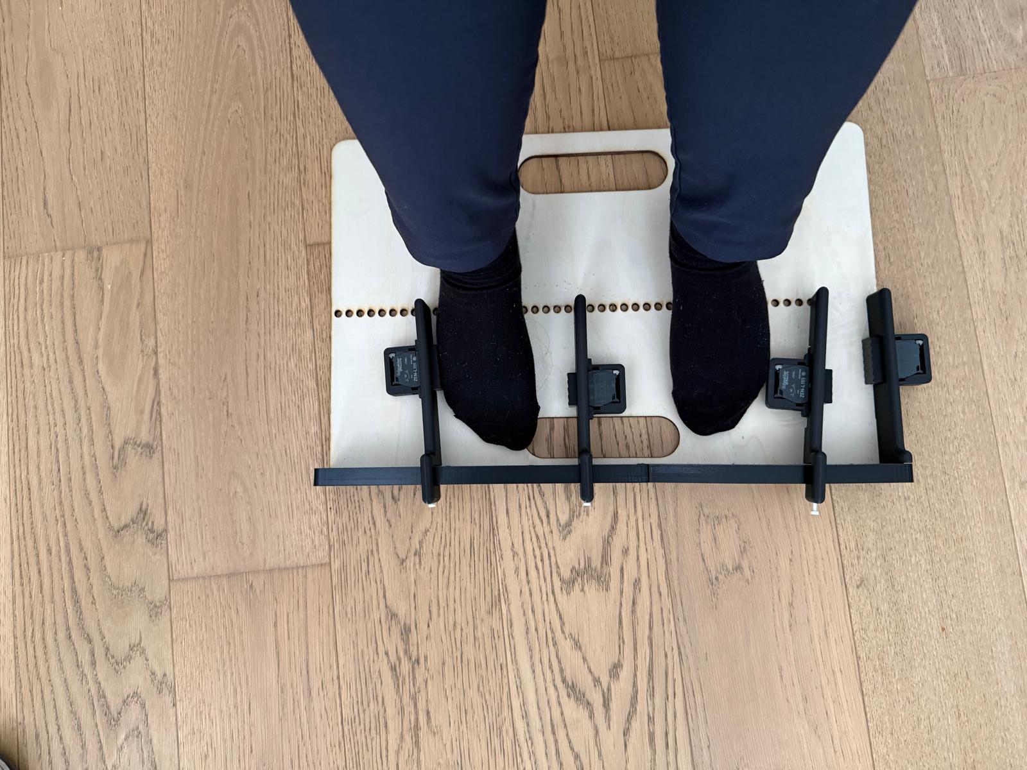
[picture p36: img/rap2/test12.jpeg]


Belangrijkste punten:
-	Gebruiker weet niet dat het product kan ingesteld worden als dit niet wordt vermeld
-	Voor de witte pinnen die de muurtjes vast houden moet een andere oplossing komen, dit pinnetje wordt zonder twijfel kwijtgeraakt als die ergens valt. (we zijn ervan bewust dat dit zo ging zijn, maar het was een voorlopige oplossing om testen te kunnen uitvoeren.)
-	Bij het afgewerkte product moet er een duidelijker verschil zijn tussen de kant van de knoppen en de kant van de behuizing.
-	De algemene oriëntatie is duidelijk voor de gebruiker
-	De inputs activeren gaat zonder problemen

Na de gebruiker wist dat het product ingesteld kon worden verliep dit minder stroef en is de definitieve gebruiksopstelling hieronder te zien.

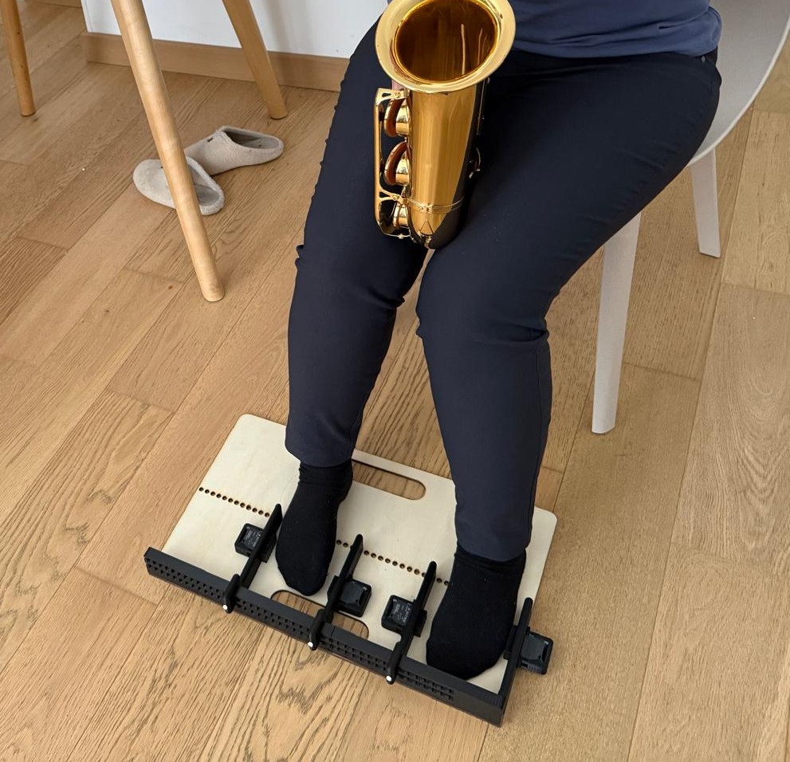
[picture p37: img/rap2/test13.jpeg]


---

### b. Test 2

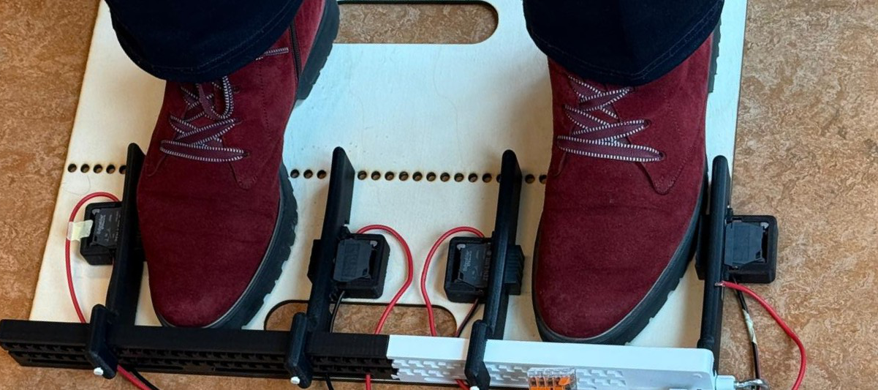
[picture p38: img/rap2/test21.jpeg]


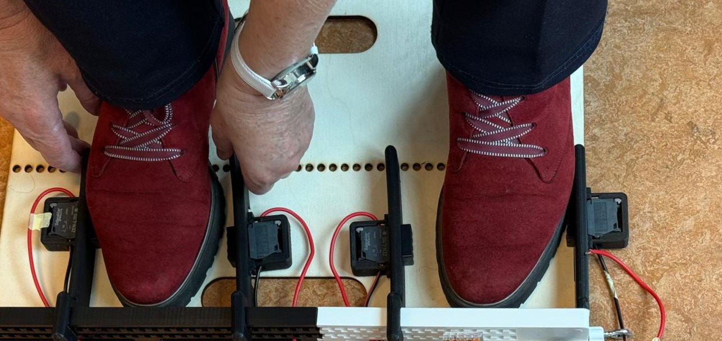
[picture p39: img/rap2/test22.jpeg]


Belangrijkste punten:
-	Het opstellen van het prototype ging voor deze persoon vlot
-	Er werd meerdere maal verbaal vermeld dat het aandrukken van de knoppen comfortabel aanvoelt
-	De witte pinnen waren opnieuw een probleem. De gebruiker probeerde het prototype in te stellen door het te verschuiven zonder te pinnen eruit te halen wat resulteerde in het krom trekken van de muurtjes (zie hierboven). Na het verwijderen van de pinnen en dit opnieuw te proberen ging het instellen vlotter.

---

## 2 Niet functionele prototype

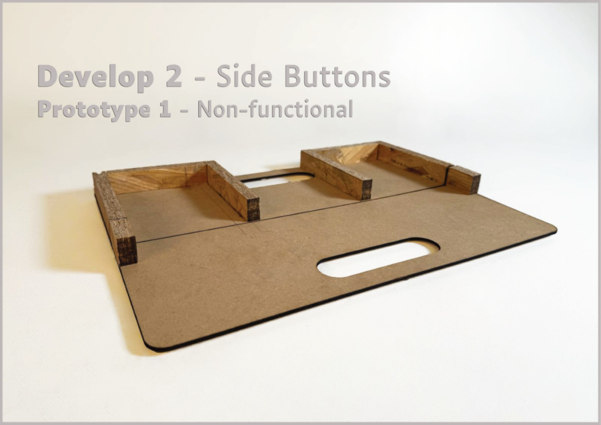
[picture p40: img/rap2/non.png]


Bij deze test werd gekeken of de gebruiker begreep of het prototype kon ingeklapt worden. Vervolgens werd gekeken of het handvat die dient om het product te dragen op een intuïtieve plaats zit. Dit werd getest om te gebruiker te vragen om 5 seconden met het product te wandelen en te kijken of op die plaats werd vast gehouden. Tenslotte werd gevraagd aan de gebruiker om het product op tafel te plaatsen op de manier waarop hij/zij denkt het meest intuïtief is. Het verwachte vouwproces en opbergpositie zijn te zien in onderstaande foto.



Het resultaat is hieronder te zien.

Belangrijkste punten:
-	Het automatisch dichtklappen is een factor die het veel intuïtiever maakt
-	Gebruiker herkend handvat spontaan
-	Ronddragen vormt geen probleem
-	Opstaande randen werden gezien als steunpunten, wat overeenkomt met de verwachte stand













## Besluit

| Nr. | Categorie | Design Requirement | Inzicht/reden |
|---:|---|---|---|
| 1 | Voetpositionering | Er moet een duidelijk tactiel verschil zijn tussen voetzones en knop-/behuizingszones. | Eén voet werd fout geplaatst tussen de binnenste muurtjes door verwarring met de knopbehuizing. |
| 2 | Instelbaarheid | De verstelbaarheid van het product moet voelbaar en vanzelfsprekend zijn. | Gebruikers merkten niet altijd dat het product kon worden ingesteld. |
| 3 | Instelbaarheid | Het verstellen van de muurtjes moet zonder losse onderdelen kunnen gebeuren. | De witte pinnen waren moeilijk voelbaar en kunnen gemakkelijk kwijtraken. |
| 4 | Instelbaarheid | De gebruiker moet tactiel kunnen voelen wanneer een onderdeel vast of los staat. | De testpersonen wisten niet meteen waarom de muurtjes niet konden bewegen. |
| 8 | Opplooien | Het product moet automatisch of semiautomatisch beginnen dichtklappen wanneer het wordt opgetild. | Dit maakte het opplooien intuïtiever en gemakkelijker. |
| 9 | Dragen | Het handvat moet geïntegreerd blijven in de vorm van het product. | De gebruiker herkende het handvat spontaan zonder uitleg. |
| 10 | Dragen | Het product moet stabiel blijven tijdens het ronddragen. | Ronddragen vormde geen probleem, maar stabiliteit blijft belangrijk voor vertrouwen. |

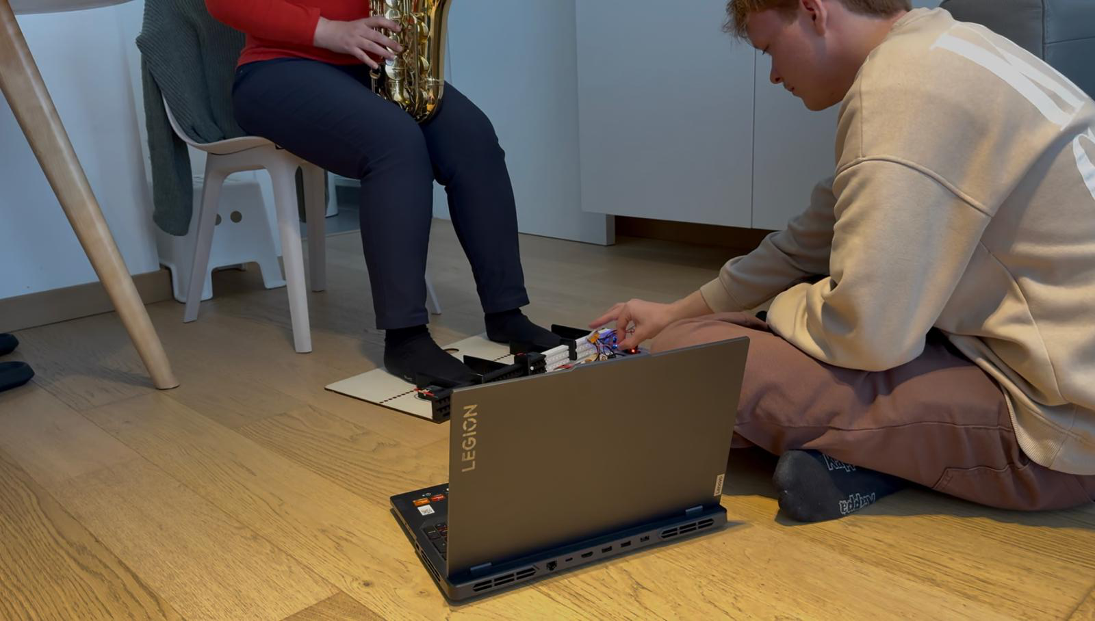
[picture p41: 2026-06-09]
img/cognitieve/testbeeld.jpeg
